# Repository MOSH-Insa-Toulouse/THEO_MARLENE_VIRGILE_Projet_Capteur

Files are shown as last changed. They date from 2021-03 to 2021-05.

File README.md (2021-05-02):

# THEO_MARLENE_VIRGILE_Projet_Capteur
Ce projet s'inscrit dans l'UF **"Du capteur au banc de Test"** en 4ème année Génie Physique, à l'INSA de Toulouse. 
***
Ce dernier a pour but l'élaboration d'un **capteur de déformation** à bas coût à base de graphite, dont le fonctionnement est basé sur le principe de déplacement des électrons entre les nanoparticules par effet tunnel. 
La contrainte mécanique appliquée modifiant la distance entre les particules, la conductivité électrique de la couche de graphite subit elle aussi une modification. La déformation du capteur créé grâce à un dépôt au crayon à papier engendre donc une variation de résistance alors mesurable.
*** 
Dans ce dossier sont présentées les différentes étapes que nous avons suivies : du design de notre shield, à notre code Arduino en passant par la réalisation d'une application pour téléphone et d'un banc de mesure réalisé en impression 3D. 

## Sommaire 

* [1. Description du projet et détail des livrables](#PremiereSection) 
* [2. Arduino](#DeuxiemeSection)
  * [2.1. Librairies utilisées](#DeuxiemeSection1)
  * [2.2. Code Arduino](#DeuxiemeSection2)
* [3. KICAD](#TroisiemeSection)  
  * [3.1 Symboles et empreintes](#TroisiemeSection1)
  * [3.2 Schématique](#TroisiemeSection2)
  * [3.3 Placement des composants](#TroisiemeSection3)
  * [3.4 Visualisation 3D](#TroisiemeSection4)
* [4. Fabrication du shield](#QuatriemeSection)
  * [4.1 Réalisation du PCB](#QuatriemeSection1)
  * [4.2 Perçage et soudure](#QuatriemeSection2)
* [5. Application Android](#CinquiemeSection) 
* [6. Tests](#SixiemeSection)
  * [6.1. Banc de test](#SixiemeSection1)
  * [6.2. Résultats obtenus](#SixiemeSection2)
  * [6.3. Analyse des résultats et discussion](#SixiemeSection3)
* [7. Datasheet](#SeptiemeSection)

## 1. Description du projet et détail des livrables

Liste des livrables :

- [x] Un code Arduino permettant une mesure de résistance et un contrôle des fonctionnalités Bluetooth, OLED... 
- [x] Un shield PCB
- [x] Une application android APK 
- [x] Un protocole du banc de test
- [x] Une datasheet des capteurs de déformation

Dans un premier temps, nous avons réalisé un **code Arduino** fonctionnel permettant de contrôler un amplificateur transimpédance, un encodeur rotatoire, un écran OLED ainsi qu'un module Bluetooth. Nous l'avons ensuite testé en effectuant nos premiers branchements.
Ensuite, nous avons réalisé le design de notre **shield** à l'aide du logiciel *KICAD*, nous l'avons fabriqué, puis nous avons assemblé nos composants dessus.   
A la suite de cela, nous avons utilisé le logiciel *MIT App Inventor* afin de développer une **application téléphone APK**, capable de communiquer et recevoir des données à distance à l'aide du module Bluetooth (notamment de récupérer la résistance ressentie par le capteur et de l'afficher sur un graphique).    
Nous avons également designé puis réalisé, un **banc de mesure** en impression 3D, qui, à l'aide d'un servomoteur nous permet de caractériser la réponse en déformation de nos futurs capteurs.   
Finalement, nous sommes passés à la phase de tests et avons créé nos capteurs, en les "coloriant" avec divers types de crayons à papier (HB,B,...). Nous avons ensuite caractérisé ces derniers en récupérant leur résistance en fonction de leur déformation, et avons ainsi pu établir une **datasheet**.

## 2. Arduino

### 2.1. Librairies utilisées

Pour développer notre code, nous avons utilisé plusieurs librairies :["Adafruit_GFX_Library"](/Librairies/Adafruit_GFX_Library) et ["Adafruit_SSD1306"](/Librairies/Adafruit_SSD1306) nous permettant le contrôle de nos modules, ainsi que la librairie [Adafruit_BusIO](/Librairies/Adafruit_BusIO) permettant de gérer la connexion en I2C et SPI.

### 2.2. Code Arduino

Le code [prog_arduino](/Programme%20Arduino/prog_arduino) développé sous Arduino IDE permet d'assurer la communication de tous les éléments de notre carte Arduino (Module Bluetooth, Oled et encodeur rotatoire) afin de réaliser des fonctions voulues. Nous avons ainsi réalisé quatre menus différents qui permettent de réaliser des tâches différentes. 

- Le premier menu permet d'afficher sur l'Oled la valeur de résistance de la jauge de contrainte traduite par l'acquisition de la tension de sortie de notre circuit électronique. Il permet aussi d'envoyer via le module bluetooth la valeur de tension mesurée entre 0 et 5 volts, sous la forme d'un nombre codé en 8 bits : 0 correspondant à 0V et 255 correspondant à 5V. L'objectif de cet envoi est d'ensuite le récupérer via notre application APK pour pouvoir traiter les données.
- Le second menu est assez similaire. La seule différence réside sur l'affichage de l'Oled. On n'affiche plus la valeur de résistance mais la valeur de tension. 
-  Le troisième menu permet de définir un temps d'acquisition sur l'application. On choisit la valeur en secondes grâce à l'encodeur rotatoire et lorsqu'on sélectionne la valeur choisie, elle s'envoie par Bluetooth pour être récupérée et enregistrée par l'application.
-  Le quatrième menu fonctionne de la même manière que le troisième mais permet de changer la valeur de R2 que l'on a laissé variable afin de s'adapter à la plage de mesure de la résistance du capteur. On entre la valeur voulue grâce à l'encodeur rotatoire. 

Les codes contenus dans les dossiers [BT_Test](/Programme%20Arduino/BT_Test), [ENC_TEST](/Programme%20Arduino/ENC_TEST) et [OLED_TEST](/Programme%20Arduino/OLED_TEST) permettent de vérifier individuellement l'état de fonctionnement de chaque module ajouté à notre shield. 

Enfin, Le code Arduino [Servomoteur](/Programme%20Arduino/Banc%20de%20test/Servomoteur) permet de contrôler notre banc de test et sera plus amplement expliqué dans la partie **6. Tests**.

## 3. KICAD

### 3.1. Symboles et empreintes
- Module Bluetooth 

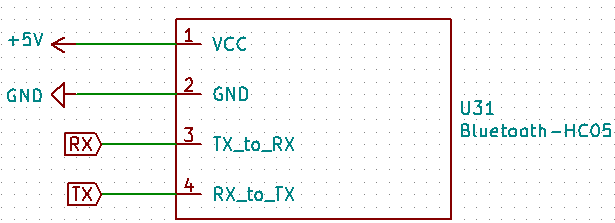
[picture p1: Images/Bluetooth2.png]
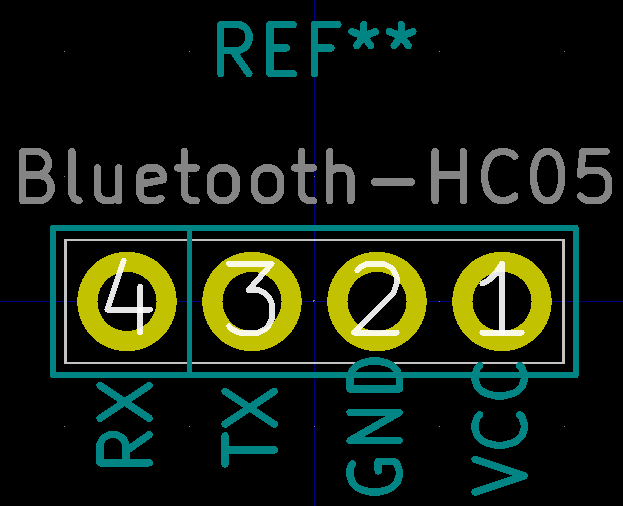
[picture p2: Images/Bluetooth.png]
 

- Encodeur rotatoire 

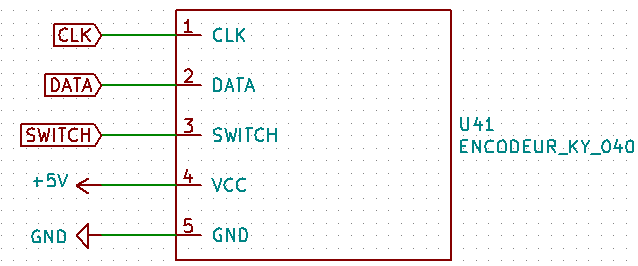
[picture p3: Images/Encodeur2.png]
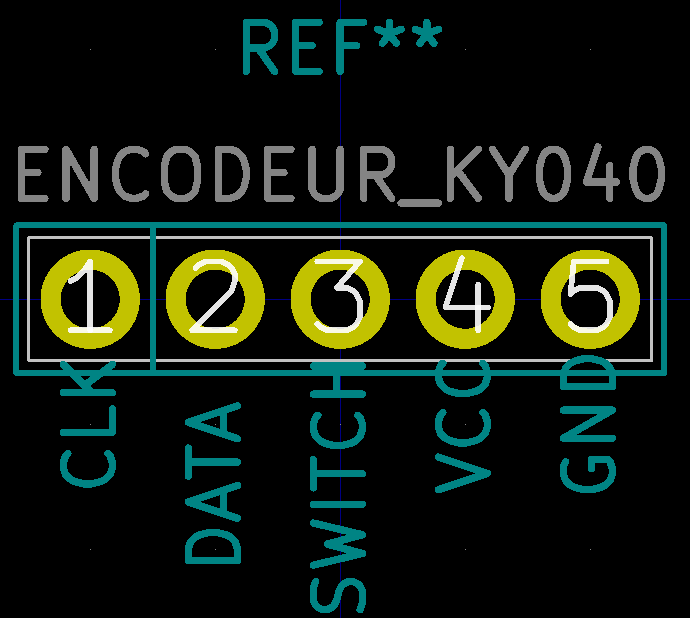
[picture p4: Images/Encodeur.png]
 

- Ecran OLED 

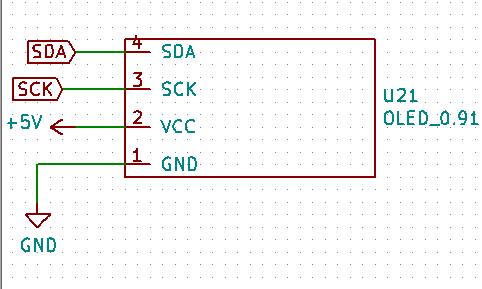
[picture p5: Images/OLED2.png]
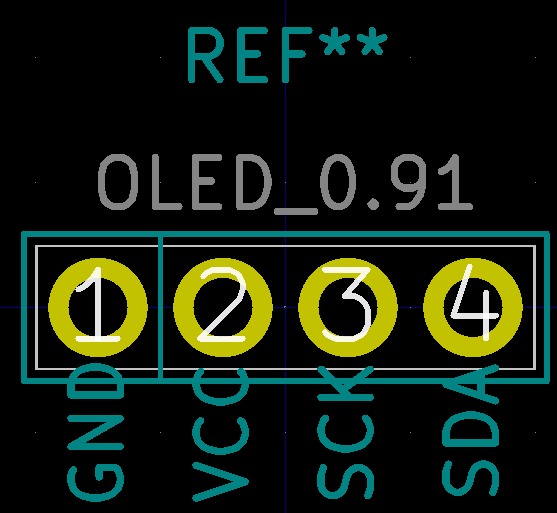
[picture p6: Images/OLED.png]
 

- Amplificateur LTC 1050

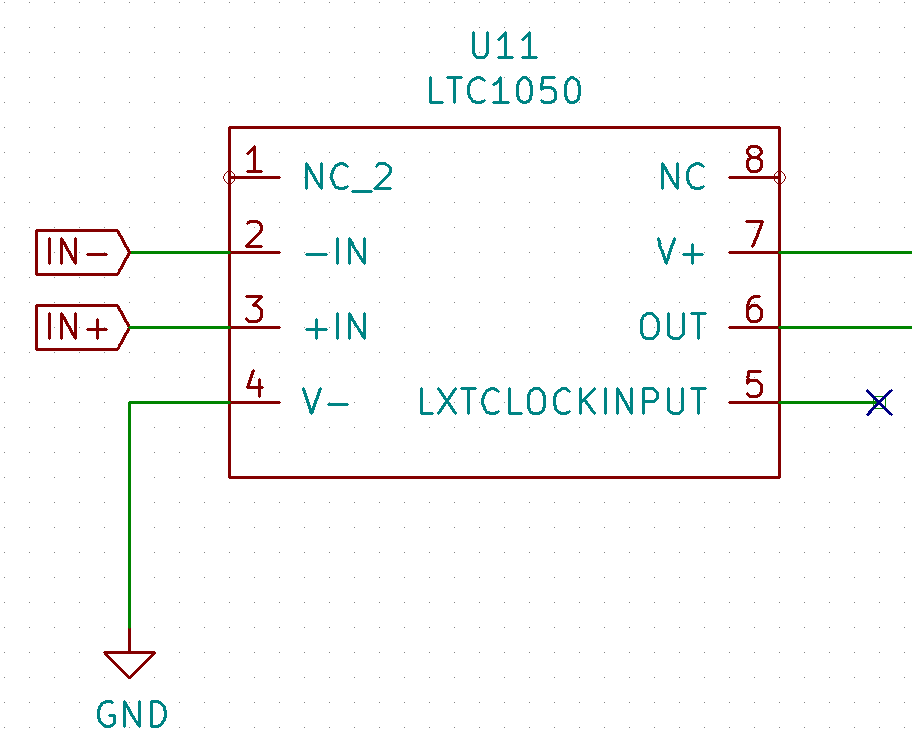
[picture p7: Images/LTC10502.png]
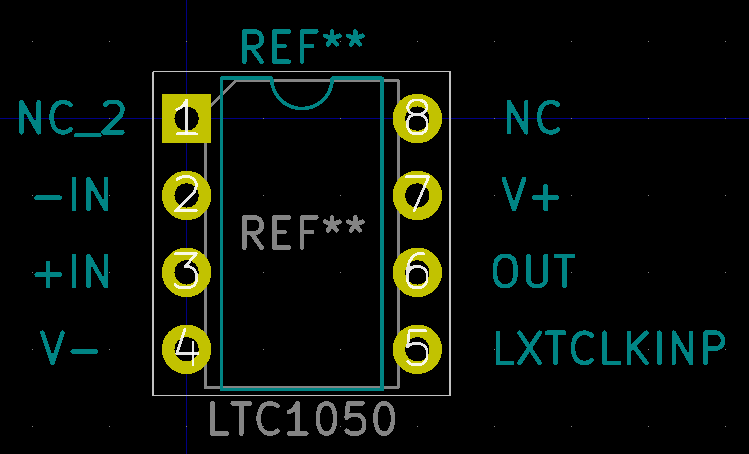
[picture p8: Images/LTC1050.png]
 

### 3.2. Schématique de l'ensemble 

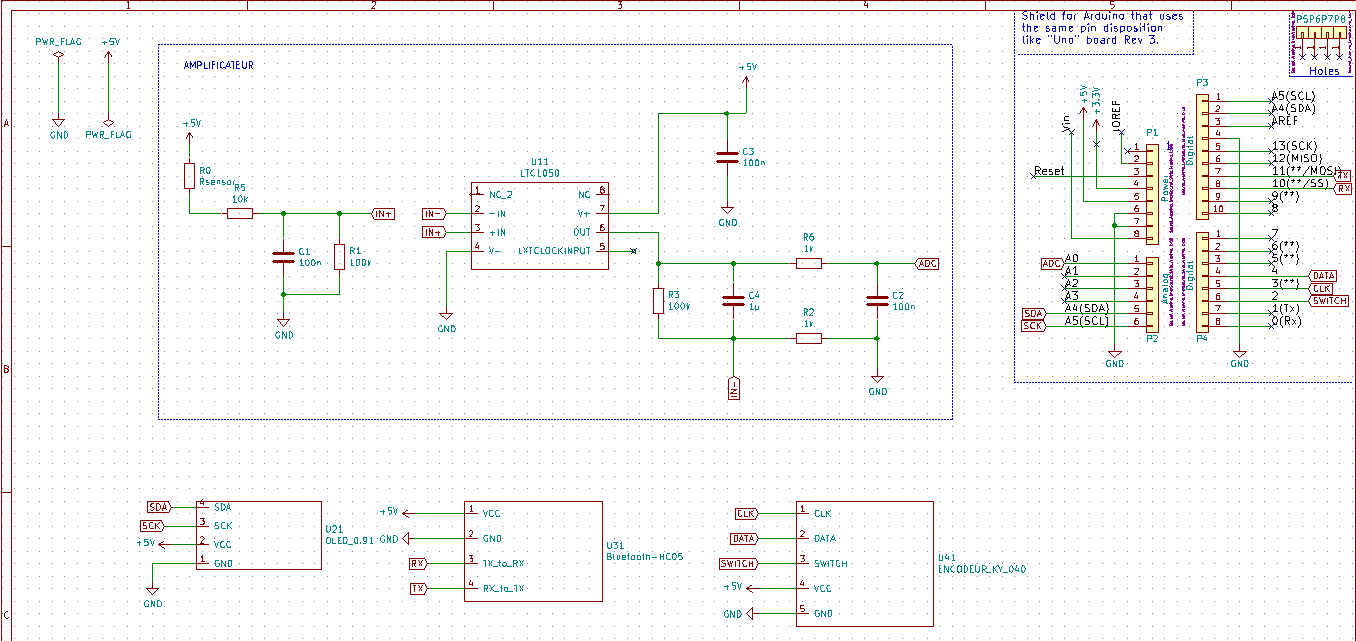
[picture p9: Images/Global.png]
Glob


Une fois les empreintes créées, nous avons pu réaliser le Eeschema de notre shield. En haut à droite sont représentées les broches de la carte Arduino. Au centre est représenté l'amplificateur transimpédance, et en bas l'écran OLED, le module Bluetooth et l'encodeur rotatoire.

### 3.3. Placement des composants
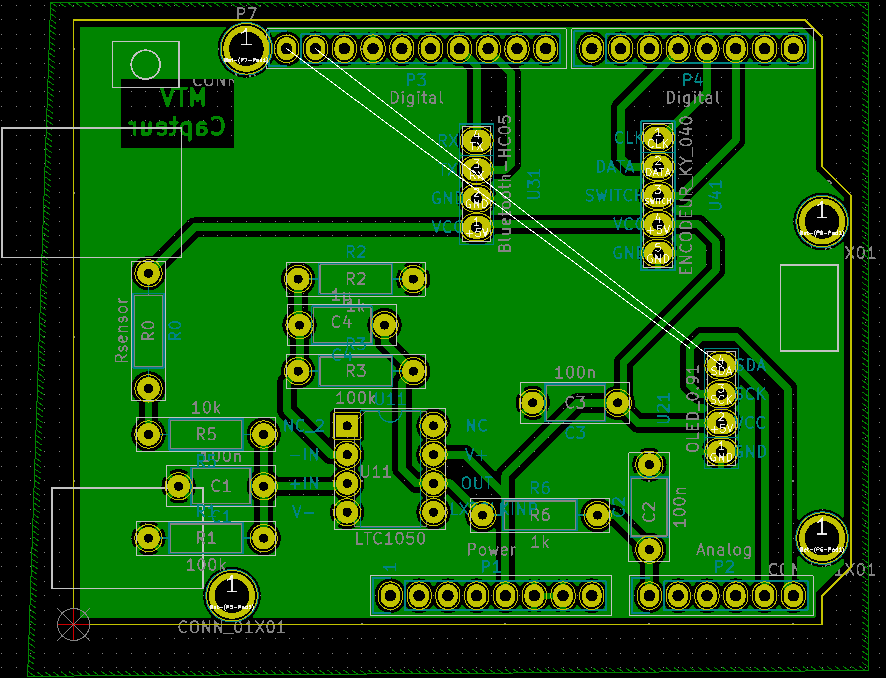
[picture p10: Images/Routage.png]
Rout


### 3.4. Visualisation 3D
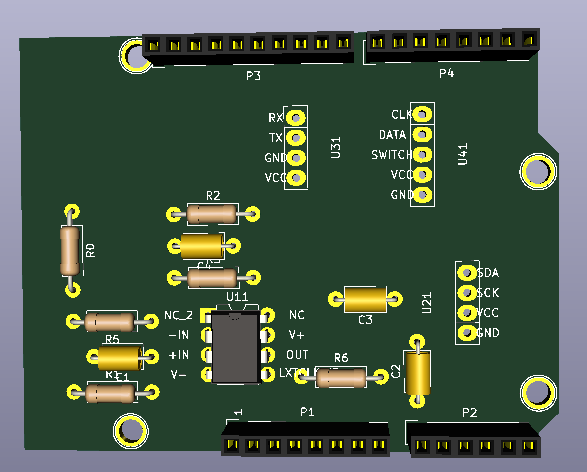
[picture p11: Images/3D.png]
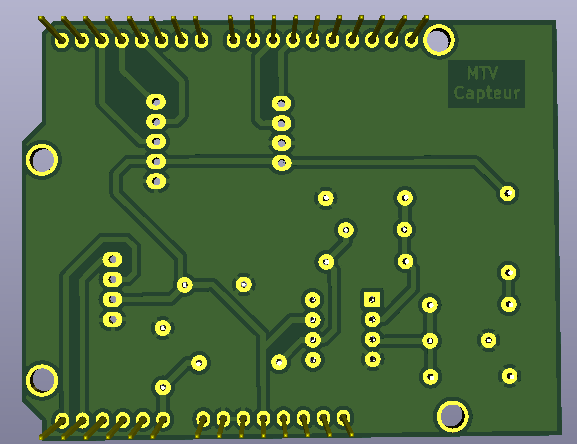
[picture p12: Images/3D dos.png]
 

## 4. Fabrication du shield
### 4.1. Réalisation du PCB

 Nous avons ensuite pu fabriquer le PCB sur une plaquette d'epoxy recouverte d'une fine couche de cuivre (environ 60µm).  
 Tout d'abord, nous avons imprimé notre modélisation du PCB sur du papier calque, puis, une insolation aux UV pendant 2 minutes a permis de transposer cette "silhouette" sur notre couche d'epoxy, permettant ainsi de déposer une résine protectrice, qui grâce à un révélateur, a pu être retirée aux endroits désirés.  
 Ensuite, la plaquette a été déposée dans un bain de perchlorure de fer afin d'être gravée (environ 8 minutes). A la suite de cela, le cuivre non protégé par la résine a alors été retiré, permettant d'obtenir le PCB modélisé en amont.  
 Pour finir, de l'acétone a été appliquée sur la plaquette pour éliminer les dernières traces de résine.

### 4.2. Perçage et soudure

Une fois le PCB réalisé, nous sommes passés au perçage de trous sur notre plaquette à l'aide d'une perçeuse électrique afin d'insérer nos composants : 
- 0.8mm de diamètre pour l'AOP, les résistances et les capacités
- 1mm de diamètre pour les connecteurs de l'Arduino et des headers des différents modules (pinces du capteur, bluetooth, encodeur rotatoire, écran OLED)

Enfin, nous avons soudé chaque composant à l'aide d'un fer à souder.

## 5. Application Android

[L'application](/Application) développée sous MIT App Inventor, un site internet permettant de designer des applications en ligne, permet d'établir la liaison entre les données relevées par l'arduino et le traitement de celles-ci, en direct puis via la création d'un fichier de données. 

Concrètement, l'application a été designée pour corréler avec le code arduino (cf 2.). Elle permet ainsi de se connecter à un module bluetooth chargé d'envoyer la tension relevée, qui sera traduite en résistance pour le capteur. Lorsque l'on est connecté, l'application est capable d'effectuer 3 tâches principales : 
- Relever la tension envoyée par Bluetooth, afficher la valeur de résistance correspondante, de manière numérique et graphique et la traduire dans un fichier texte. Cette fonction est commandée par un système Start/Stop.
- Effectuer une acquisition selon un temps donné. Il faut au préalable définir le temps d'acquisition via l'arduino. Ce temps vient remplacer le Start/Stop, sinon la fonction est la même que précédemment.
- Modifier la valeur de résistance de R2. Pour cela, il faut rentrer la valeur via l'arduino.

## 6. Tests
### 6.1. Banc de test

Pour réaliser nos tests, nous avons utilisé 2 bancs différents ; l'un déjà existant et pensé par nos prédécesseurs et un autre par nos soins lors de la réalisation du projet.

#### Le [banc de test](/Banc%20de%20test) que nous avons imaginé a été modélisé via un logiciel de CAO et ensuite imprimé grâce à une imprimante 3D. 

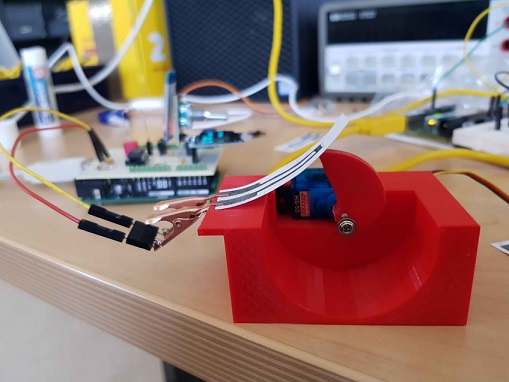
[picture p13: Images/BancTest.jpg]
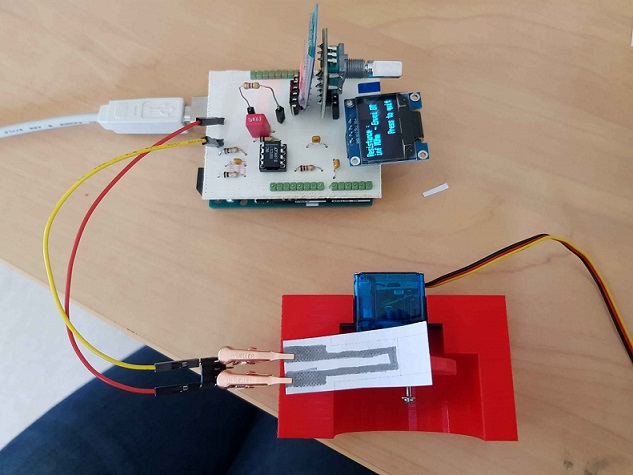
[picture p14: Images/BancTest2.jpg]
   

Il permet de mesurer la déformation du capteur en fonction du temps grâce à une rotation induite par un servomoteur et répond à deux problématiques :
 - La première étant la limite principale du banc de test déjà existant : il était destructif. En effet à chaque utilisation de celui-ci le capteur devenait inutilisable par la suite. Il nous était donc impossible de revenir aux valeurs initiales de résistances après passage du capteur sur le banc de test. 
- La seconde étant la volonté d’observer l’évolution en dynamique de la réponse du capteur afin de déterminer une potentielle fatigue de celui-ci lors d’un test cyclique. 

Nous avons donc réfléchi à un design permettant une installation fixe du capteur qui ne nécessitait plus d’action extérieure au cours de la mesure, et qui pouvait faire périodiquement une application de contrainte identique sur notre capteur. Pour cela, notre banc a été conçu en 3 parties : le socle, la pièce « escargot » et le servomoteur, pilotés via [un code Arduino](/Programme%20Arduino/Banc%20de%20Test/Servomoteur) supplémentaire. 

**Le socle**

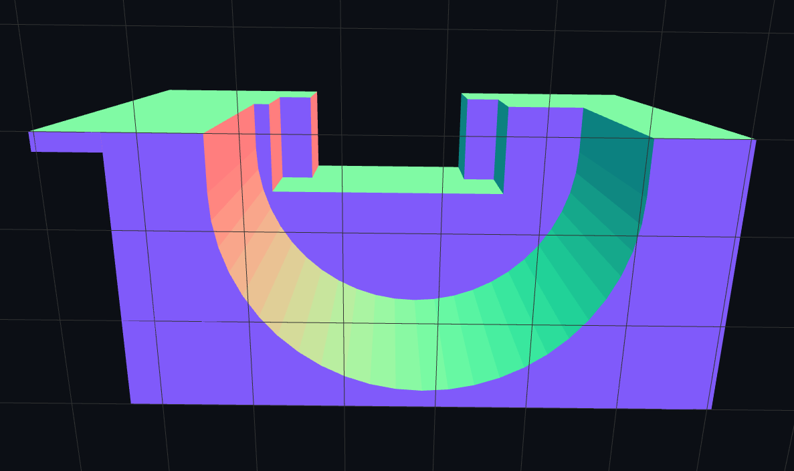
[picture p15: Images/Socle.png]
 
Le socle est la pièce massive qui permet de fixer le servomoteur et le capteur afin de ne pas avoir à retoucher le système entre les mesures.  

•	 La languette sur le côté gauche représente la zone permettant de fixer le capteur à l’aide des pinces conductrices.   
•	 Le demi cercle vide au milieu de la pièce correspond à la zone permettant la rotation de la pièce « escargot ».  
•	 L’encoche qui traverse la pièce dans la largeur permet de glisser le servomoteur et de le maintenir dans la position souhaitée.  

**La pièce « escargot »**

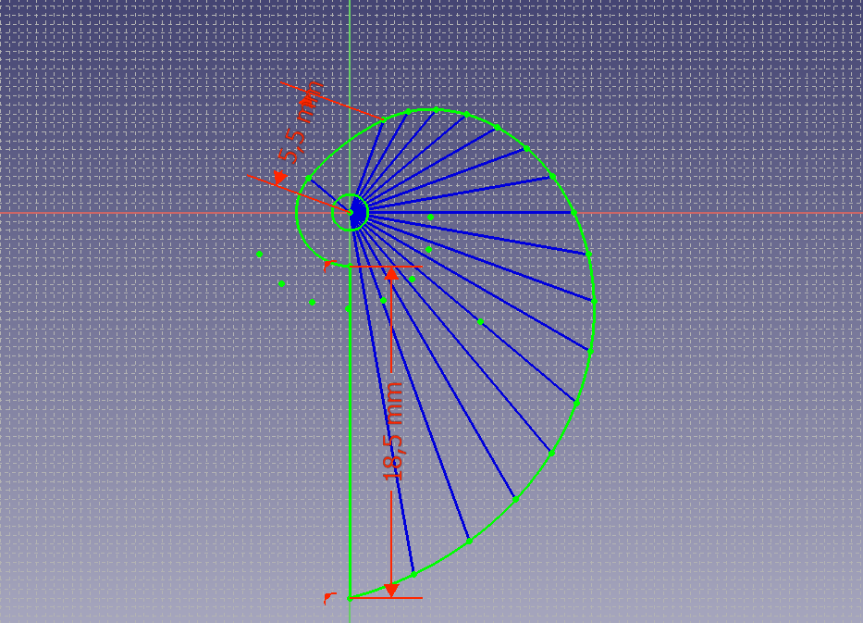
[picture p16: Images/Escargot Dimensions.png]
 

Cette pièce est un embout pour le servomoteur : l’extrémité libre du capteur repose dessus lorsqu’il est fixé sur le banc. 
Le rayon de l’embout augmente d’un millimètre tous les dix degrés de rotation ce qui permet d’avoir une variation du rayon entre 5,5 mm et 21,5 mm sur l’ensemble de la rotation du servomoteur.   

Nous souhaitions pouvoir remonter à la déformation en connaissant la longueur du rayon or après plusieurs tentatives, nous nous sommes rendus compte qu’il était difficile de remonter à cette valeur en compression avec la composition géométrique de ce banc de test.   

**Le servomoteur**

Nous avons choisi d’utiliser le servomoteur SG90 car parmi ceux à notre disposition, c’est celui dont les dimensions étaient les plus adaptées pour notre capteur.   
En effet sa petite taille nous permet d’y fixer un embout de plus petite taille qui nous assure de rester dans le domaine de la déformation élastique du papier puisque nous pouvons  appliquer des déformations plus faibles et plus précises.   
Utiliser un servomoteur nous permet de gérer facilement la rotation de la pièce «escargot», et in extenso de fixer facilement la plage de déformation du capteur à l’aide du code Arduino. 

**Le code Arduino**

Nous avons utilisé [ce code Arduino](/Programme%20Arduino/Banc%20de%20test/Servomoteur) qui nous permet de changer la plage de rotation du servomoteur. Il nous permet en modifiant les lignes 17 et 22 de changer la plage de rotation du servomoteur. L’objectif étant de balayer la plus grande différence de rayon possible tout en ne dépassant jamais le bout de course de la pièce escargot afin de ne pas détruire le capteur.  

#### Le banc de test déjà réalisé composé de 7 demi-cercles dont les rayons varient de 1 à 2,5 cm. 
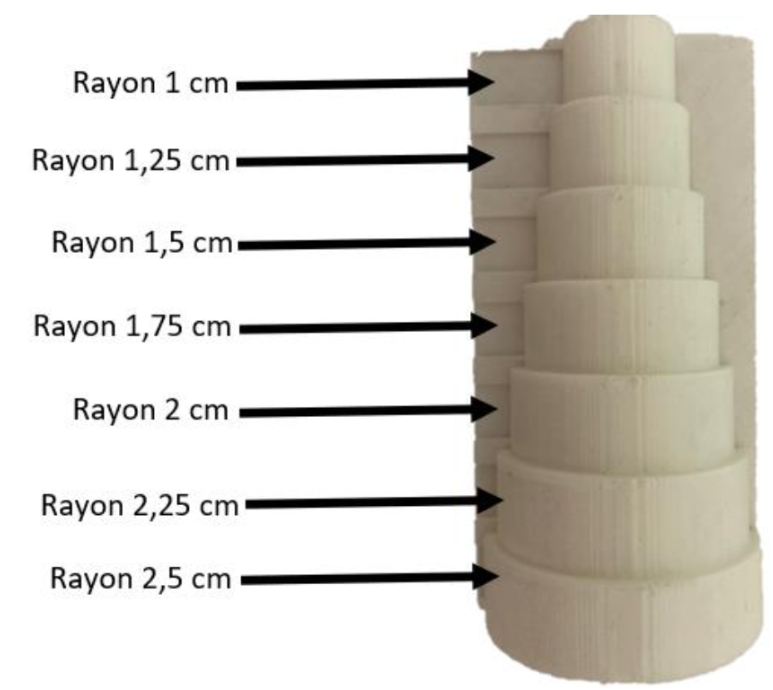
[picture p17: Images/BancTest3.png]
 

### 6.2. Résultats obtenus

**Avec le banc de test utilisant le servomoteur**

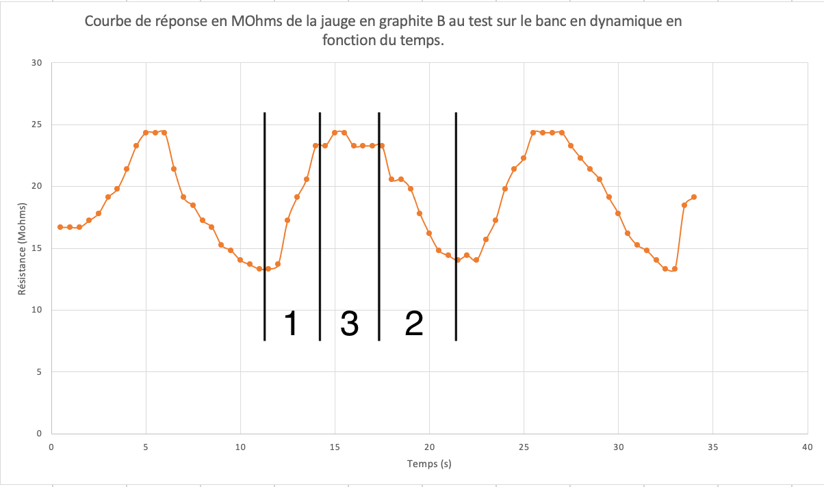
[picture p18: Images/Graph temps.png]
   

Nous pouvons voir que la jauge réagit de façon périodique à la contrainte du banc en dynamique. 
En effet, lors de la diminution du rayon de la pièce en escargot, nous observons une augmentation quasi-linéaire de la résistance (cf courbe ci-dessus zone 1). 
Lors de l'augmentation de celui-ci, nous observons une diminution quasi-linéaire de la résistance de la jauge de contrainte (cf courbe ci-dessus zone 2).
Nous observons également une plage de données instable entre ces deux phases. Cette réponse du capteur est due à l’imperfection de notre banc (cf courbe ci-dessus zone 3). En effet, lorsque l’on arrive au bout de la course du servomoteur, le capteur ne suit pas complètement l’évolution du rayon de courbure, et entre en contact avec une autre surface de la pièce en « escargot » que celle souhaitée. 

**Avec le banc de test déjà réalisé**

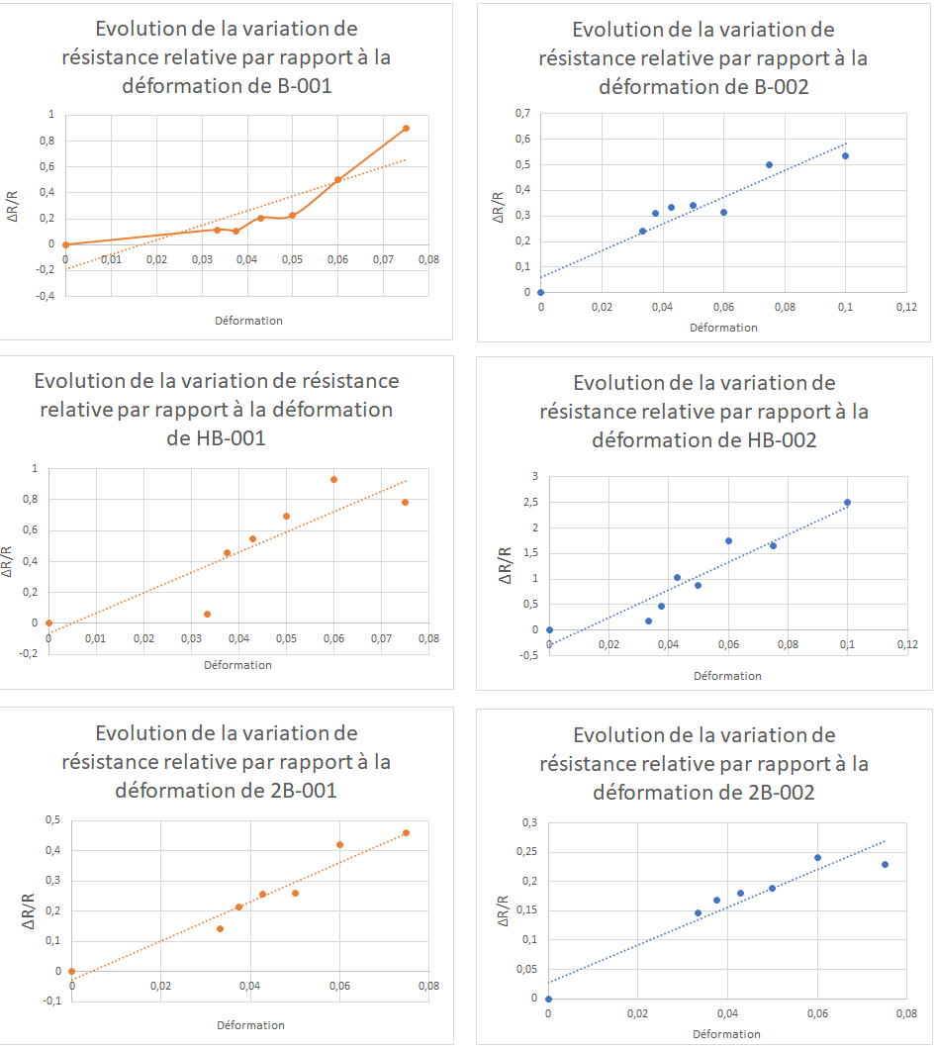
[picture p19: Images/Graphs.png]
 

Comme nous pouvons l’observer sur les graphiques ci-dessus, la plupart des réponses des jauges aux déformations appliquées à l’aide du banc de test statique suivent une évolution quasi-linéaire. 

La résistance sans contrainte varie du simple au double entre deux jauges produites par le même type de crayon à papier. 

Les variations de résistance sont plus importantes lorsque la dureté du crayon est plus élevée. En effet, pour le HB nous avons pu observer au maximum une variation de 5 à 20 MOhms et pour le 2B de 4 à 5 MOhms. 

Les facteurs de jauge obtenus en faisant une approximation linéaire sont de :
- 6,5 et 3,2 pour les essais 1 et 2 avec des jauges dessinées avec des crayons 2B
- 6,1 et 11,4 pour les essais 1 et 2 avec des jauges dessinées avec des crayons B
- 13,1 et 27,2 pour les essais 1 et 2 avec des jauges dessinées avec des crayons HB

### 6.3. Analyse des résultats et discussion

Nous observons à l’aide de **notre banc de test** utilisant le servomoteur que le capteur retrouve sa valeur initiale de résistance entre chaque mise sous contrainte. Nous n’observons donc pas de fatigue de la jauge dans la gamme de contraintes que nous appliquons : il faudrait effectuer des tests sur de très longues périodes avant d’apercevoir d’éventuelles fatigues. 

Concernant les imprécisions de la zone de mesure se situant en bout de course du servomoteur, plusieurs améliorations sont envisageables : 
 - Concevoir la pièce « escargot » en miroir, de façon à toujours avoir un rayon plus petit sous la jauge au lieu du contraire actuellement
 - Repenser la pièce afin de pouvoir fixer directement l’extrémité du capteur à la pièce « escargot »

Nous aurions pu également réfléchir en amont au calcul de contrainte qui aurait été plus pertinent qu’un simple relevé de résistance.  
  
Ces différents résultats mettent en valeur les avantages et les limites de ce type de jauges de contrainte.   

Pour ce qui est du **banc de test déjà réalisé**, nous constatons que les jauges réalisées ont, d'après les essais, des facteurs de jauge très élevés avec l’utilisation de crayons à papier à pointe dure, mais que, si le crayon dépose trop peu de graphite, des problèmes de continuité électrique se posent.  

Une des principales limites est donc la dépose du graphite. En effet, nous remarquons des différences de quasiment un facteur 2 entre les facteurs de jauge des capteurs dessinés en 2B, B et HB. 
Ces différences peuvent être dûes à :
 - la non-répétabilité de la mesure et la destruction du capteur en fonction de la manipulation de la jauge et du banc
 - le dépôt de graphite sur le papier : la pression avec le crayon à papier, le nombre de passages du crayon, la précision du tracé    

Il faudrait réfléchir à un procédé permettant un dépôt uniforme, précis et répétable. Une impression mécanique automatisée serait une option pour rendre les facteurs de jauge plus constants.  

Nous pouvons tout de même conclure que la confection de jauges de contrainte en graphite est réalisable et permet de créer des jauges avec de très bon facteurs de jauge. 
Néanmoins, le processus de dessin doit être optimisé car il y a beaucoup trop de paramètres qui ne permettent pas de garantir la qualité de la jauge de contrainte. 

## 7. Datasheet

La [Datasheet](/Datasheet) présente l'ensemble des caractéristiques des jauges que nous avons réalisées ainsi que du shield qui permet de traduire un relevé de tension en mesure de résistance. L'objectif final est de revenir à une mesure de déformation.

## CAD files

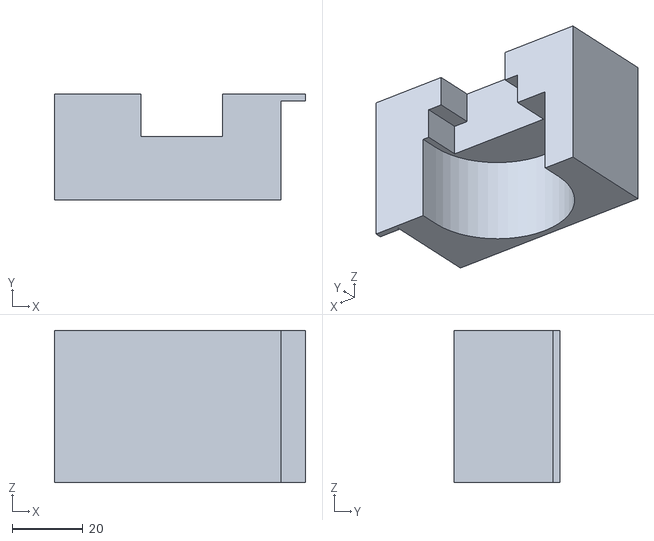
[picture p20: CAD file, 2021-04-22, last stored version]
Banc de test/socle final.stl
71.0 x 30.0 x 43.0

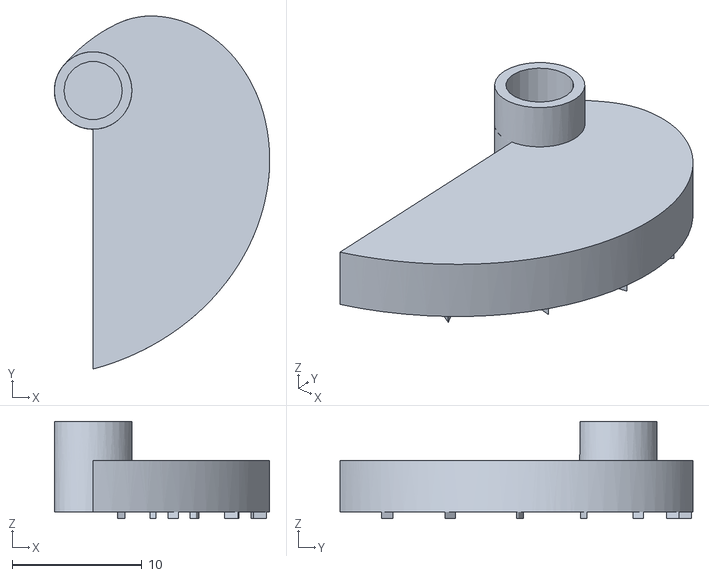
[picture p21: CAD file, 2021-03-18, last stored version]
Banc de test/pièce servomoteur.stl
16.6 x 27.3 x 7.50

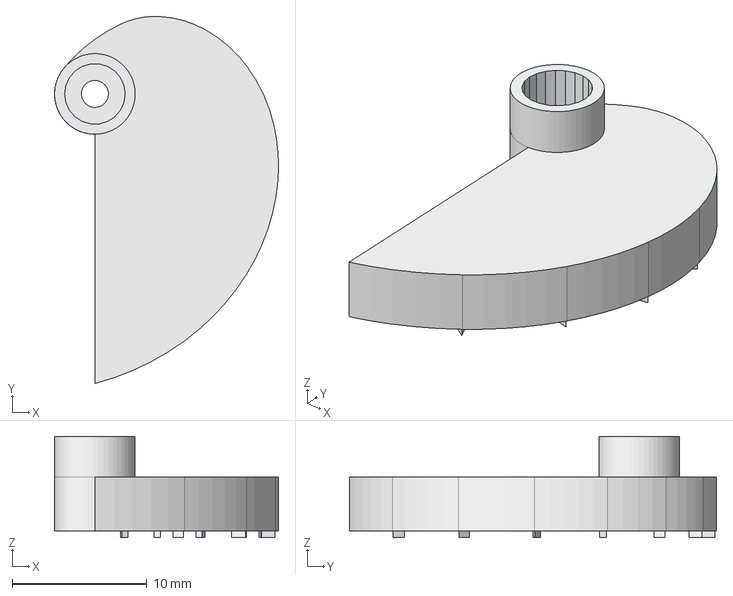
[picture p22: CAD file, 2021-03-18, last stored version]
THEO_MARLENE_VIRGILE_Projet_Capteur-main/Banc de test/Piece_Servomoteur.FCStd
16.6 x 27.2 x 7.50 mm

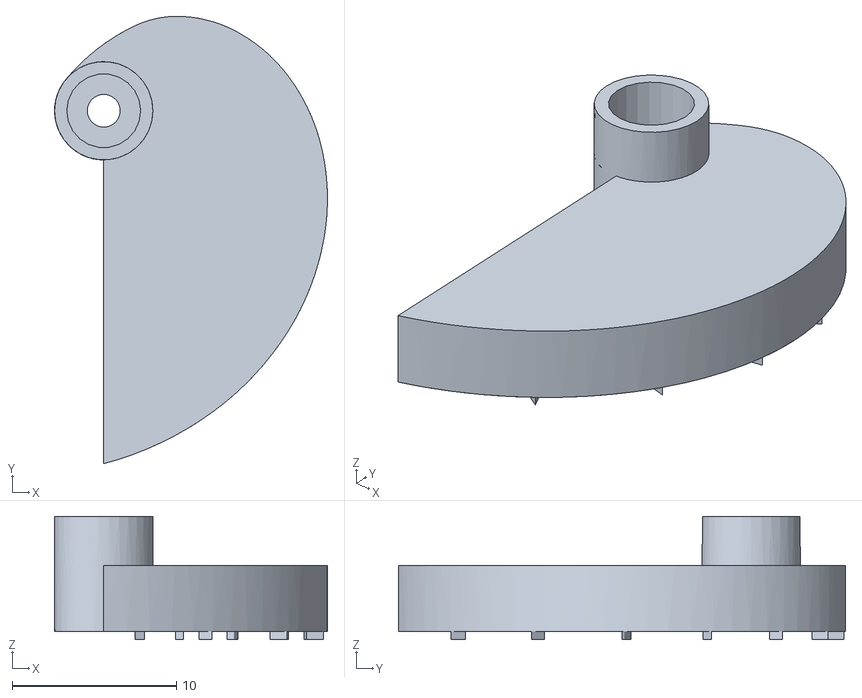
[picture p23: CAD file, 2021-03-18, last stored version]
Banc de test/Pièce servomoteur v2.stl
16.6 x 27.3 x 7.50

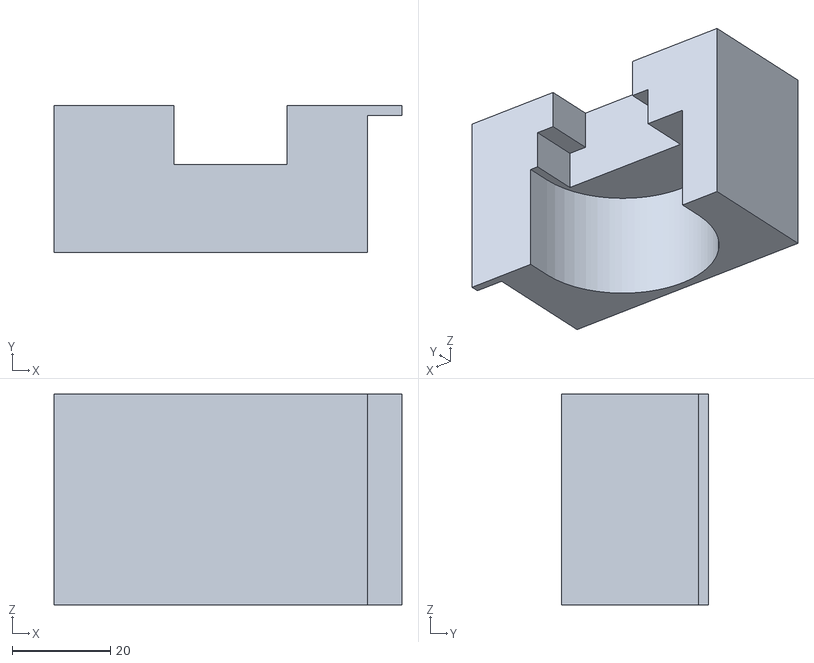
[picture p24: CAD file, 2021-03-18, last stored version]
Banc de test/socle banc test.stl
71.0 x 30.0 x 43.0

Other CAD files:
THEO_MARLENE_VIRGILE_Projet_Capteur-main/Banc de test/socle banc de test.FCStd
Banc de test/socle banc de test.FCStd

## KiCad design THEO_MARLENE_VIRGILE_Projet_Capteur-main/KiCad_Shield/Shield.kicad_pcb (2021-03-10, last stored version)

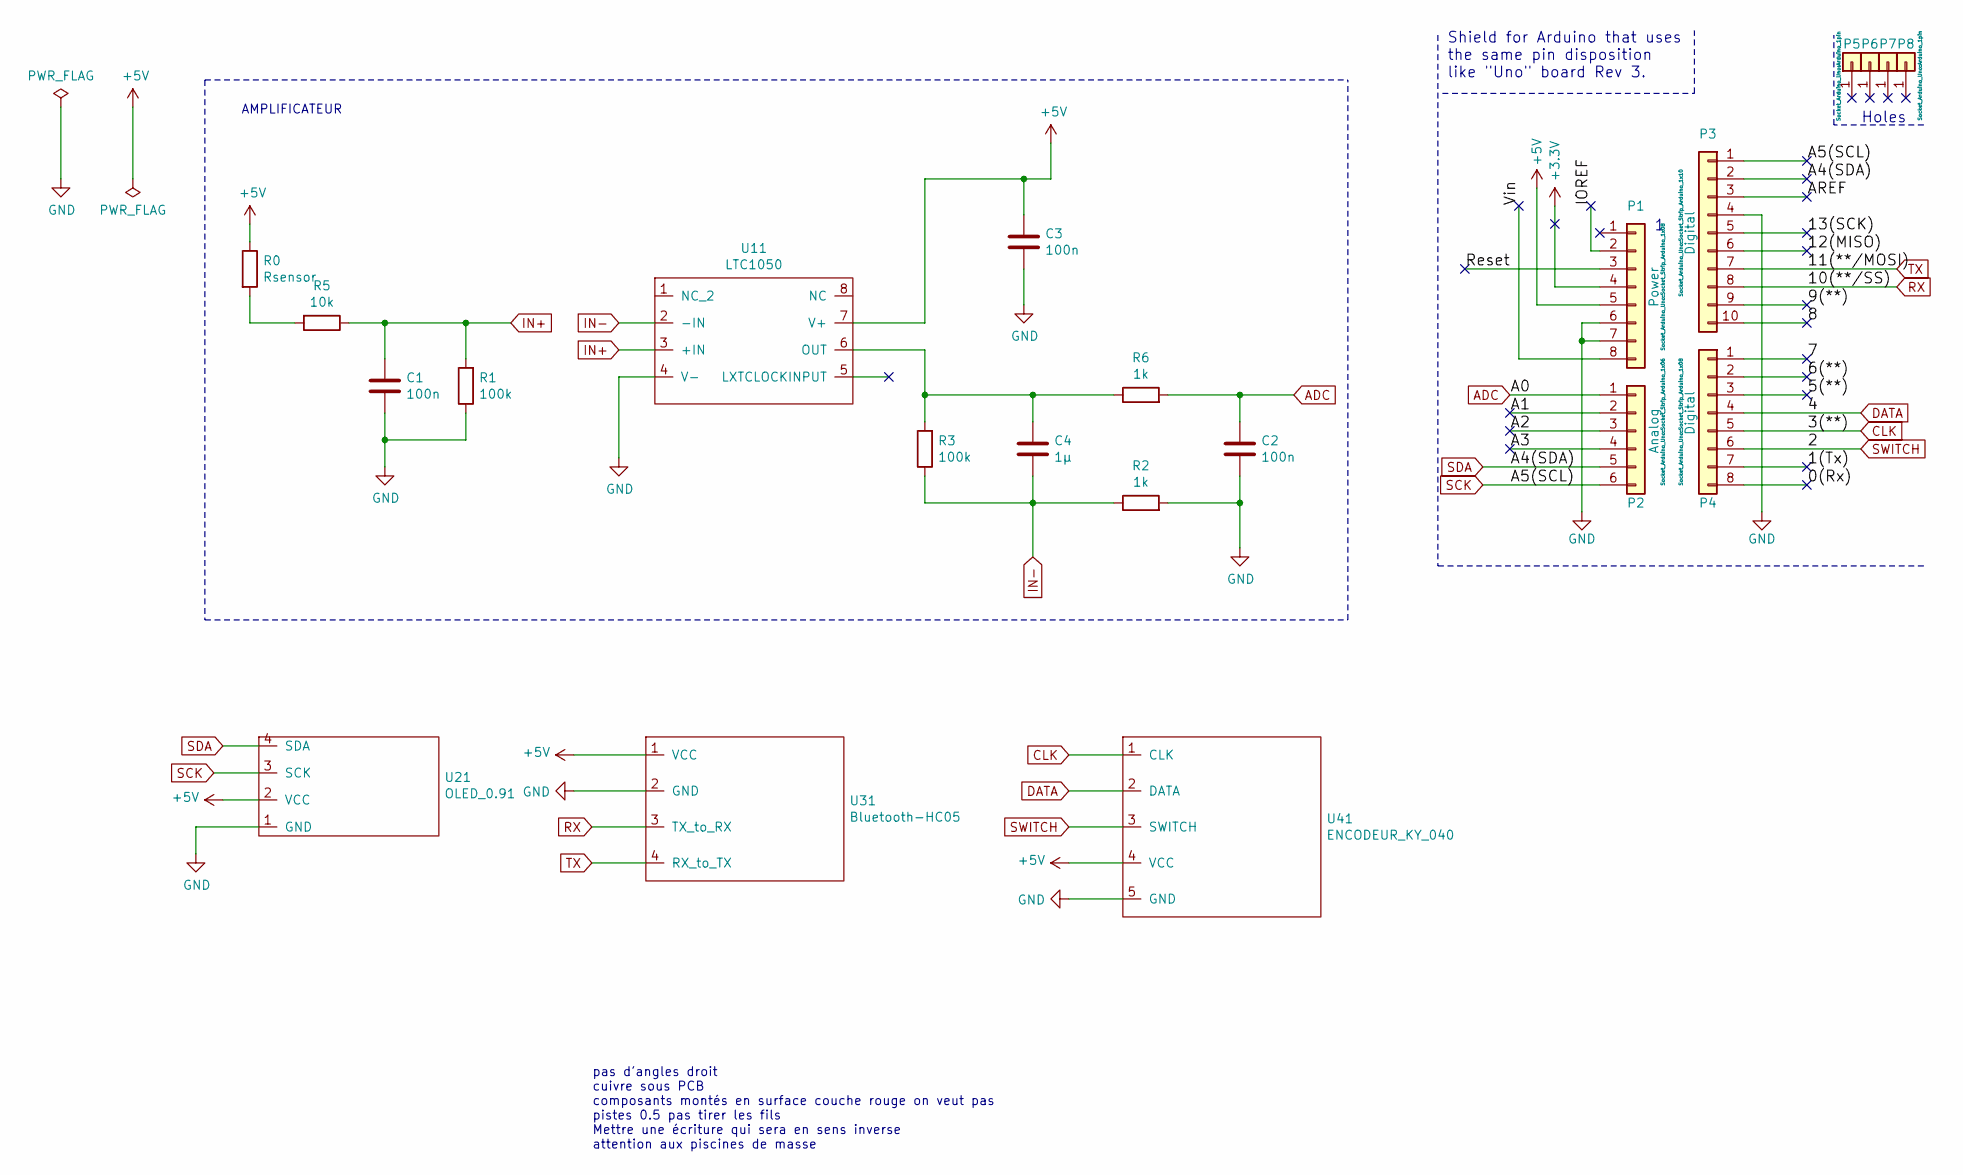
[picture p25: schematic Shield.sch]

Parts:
C1, C2, C3: 100n; C_Axial_L5.1mm_D3.1mm_P7.50mm_Horizontal
C4: 1µ; C_Axial_L5.1mm_D3.1mm_P7.50mm_Horizontal
P1: Power; Socket_Strip_Arduino_1x08
P2: Analog; Socket_Strip_Arduino_1x06
P3: Digital; Socket_Strip_Arduino_1x10
P4: Digital; Socket_Strip_Arduino_1x08
P5, P6, P7, P8: CONN_01X01; Arduino_1pin
R0: Rsensor; R_Axial_DIN0207_L6.3mm_D2.5mm_P10.16mm_Horizontal
R1, R3: 100k; R_Axial_DIN0207_L6.3mm_D2.5mm_P10.16mm_Horizontal
R2, R6: 1k; R_Axial_DIN0207_L6.3mm_D2.5mm_P10.16mm_Horizontal
R5: 10k; R_Axial_DIN0207_L6.3mm_D2.5mm_P10.16mm_Horizontal
U11: LTC1050
U21: OLED_0.91
U31: Bluetooth-HC05
U41: ENCODEUR_KY_040; ENCODEUR_KY040

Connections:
+3V3: P1.4
+5V: C3.1, P1.5, R0.1, U11.7 (V+), U21.2 (VCC), U31.1 (VCC), U41.4 (VCC)
/0(Rx): P4.8
/1(Tx): P4.7
/5(**): P4.3
/6(**): P4.2
/7: P4.1
/8: P3.10
/9(**): P3.9
/12(MISO): P3.6
/13(SCK): P3.5
/A1: P2.2
/A2: P2.3
/A3: P2.4
/AREF: P3.3
/IOREF: P1.2
/Reset: P1.3
/Vin: P1.8
ADC: C2.1, P2.1, R6.2
CLK: P4.5, U41.1 (CLK)
DATA: P4.4, U41.2 (DATA)
GND: C1.2, C2.2, C3.2, P1.6, P1.7, P3.4, R1.1, R2.2, U11.4 (V-), U21.1 (GND), U31.2 (GND), U41.5 (GND)
IN+: C1.1, R1.2, R5.1, U11.3 (+IN)
IN-: C4.2, R2.1, R3.1, U11.2 (-IN)
unnamed: C4.1, R3.2, R6.1, U11.6 (OUT)
unnamed: R0.2, R5.2
RX: P3.8, U31.3 (TX_to_RX)
SCK: P2.6, P3.1, U21.3 (SCK)
SDA: P2.5, P3.2, U21.4 (SDA)
SWITCH: P4.6, U41.3 (SWITCH)
TX: P3.7, U31.4 (RX_to_TX)

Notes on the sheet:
Holes
Shield for Arduino that uses the same pin disposition like "Uno" board Rev 3.
AMPLIFICATEUR
pas d'angles droit cuivre sous PCB composants montés en surface couche rouge on veut pas pistes 0.5 pas tirer les fils Mettre une écriture qui sera en sens inverse attention aux piscines de masse

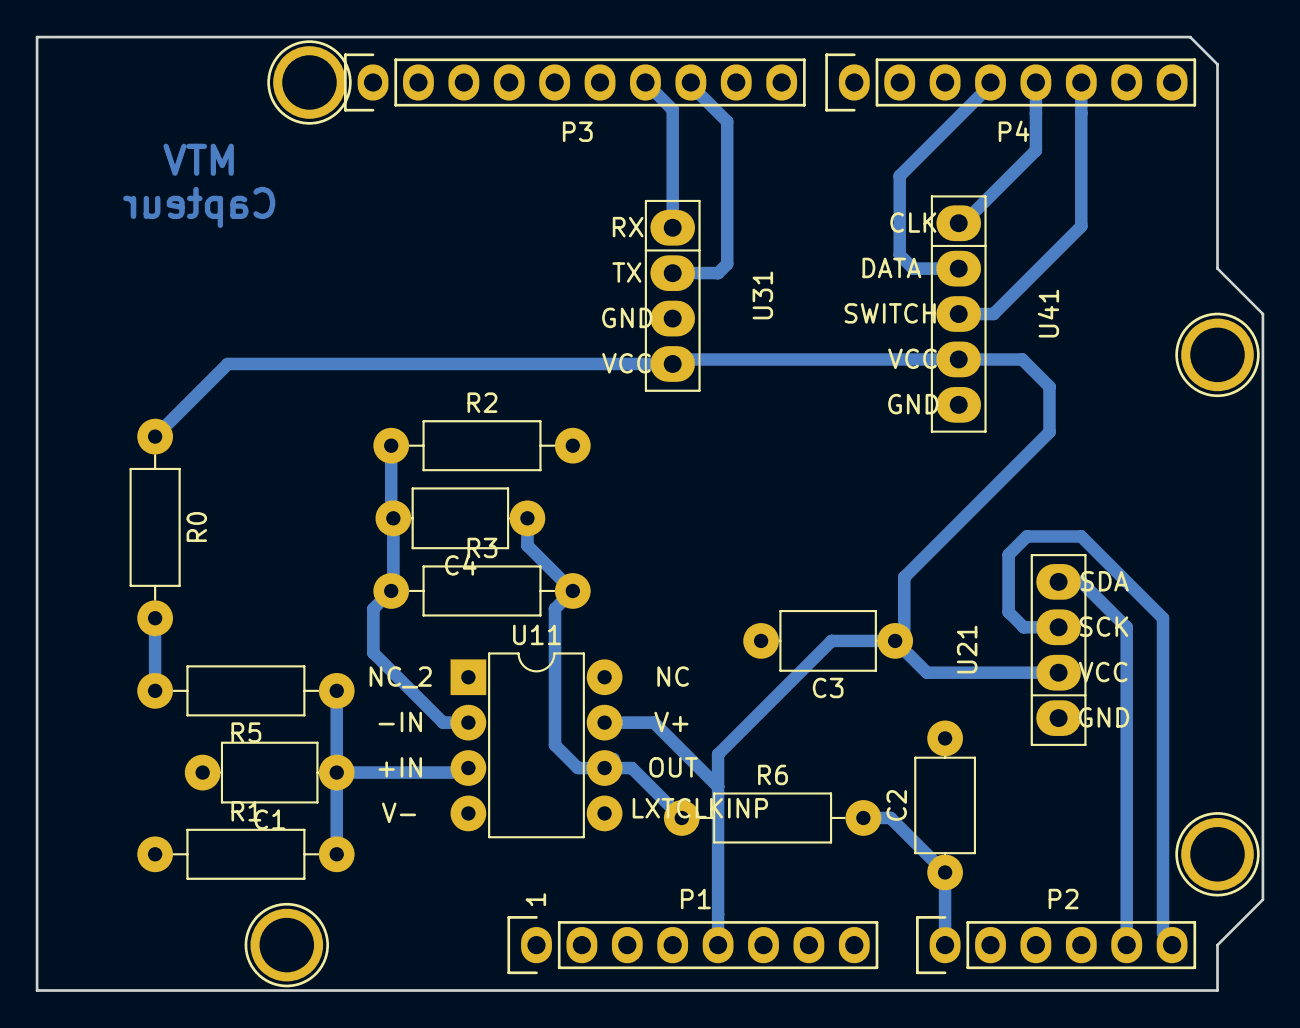
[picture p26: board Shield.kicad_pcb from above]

Board: 2 copper layers, 68.6 x 53.3 mm, 22 parts (0 on the bottom side), 14 nets.

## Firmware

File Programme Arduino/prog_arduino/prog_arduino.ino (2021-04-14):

  // Rotary Encoder

#define encoder0PinA  3  //CLK Output A Do not use other pin for clock as we are using interrupt
#define encoder0PinB  4  //DT Output B
#define Switch 2 // Switch connection if available
volatile unsigned int encoder0Menu_temp = 0;
volatile unsigned int encoder0Menu = 0;
volatile unsigned int Menu_State = 0 ;

volatile unsigned int action_encoder = 0; // retient quelle action effectuer pour l'encodeur
volatile unsigned int temps_acquisition_temp = 0;
volatile unsigned int temps_acquisition = 0;

volatile unsigned int val_R2_temp = 0;
volatile unsigned int val_R2 = 0;

int val_choisie = 0;
int temps_choisi = 0;

int State;
int Old_State;

  // Oled 

  // if any problem occurs make Ctrl+Maj+i and add Adafruit_BusIO_Register , Adafruit_SSD1306 , Adafruit_GFX

#include <Wire.h>
#include <Adafruit_GFX.h>
#include <Adafruit_SSD1306.h>
#include <Adafruit_BusIO_Register.h>
#include <Adafruit_I2CDevice.h>
#include <Adafruit_I2CRegister.h>
#include <Adafruit_SPIDevice.h>


#define SCREEN_WIDTH 128 // OLED display width, in pixels
#define SCREEN_HEIGHT 32 // OLED display height, in pixels

// Declaration for an SSD1306 display connected to I2C (SDA, SCL pins)
#define OLED_RESET 4 // Reset pin # (or -1 if sharing Arduino reset pin)
#define SCREEN_ADDRESS 0x3C ///< See datasheet for Address; 0x3D for 128x64, 0x3C for 128x32
Adafruit_SSD1306 display(SCREEN_WIDTH, SCREEN_HEIGHT, &Wire, OLED_RESET);

  // Bluetooth

#include <SoftwareSerial.h>
#define rxPin 10 //Broche 10 en tant que RX, � raccorder sur TX du HC-05
#define txPin 11 //Broche 11 en tant que RX, � raccorder sur TX du HC-05
#define baudrate 9600 
SoftwareSerial Serial_Phone(rxPin ,txPin); //D�finition du software serial

  // Transimp

#define ADCpin  0

  // Global variables 

float resistance = 0;
float tension;
int R1 = 100;
int R2 = 22;
int R3 = 100;
int R5 = 10;
int voltage_ADC;


  // Fonctions Encodeur

// doEncoder increments or decrements the variable encoder0Menu that is used to navigate into menues, between 4 of them, also used to increments the "temps_acquisition" variable
void doEncoder() {

  State = digitalRead(encoder0PinA);

  if (action_encoder == 0) {
  
    if (State != Old_State)
    {
      if (digitalRead(encoder0PinB) != State)
      {
        encoder0Menu_temp = (encoder0Menu_temp + 1) % 8;
        encoder0Menu = encoder0Menu_temp/2;
      }
      else {
        encoder0Menu_temp = (encoder0Menu_temp - 1) % 8;
        encoder0Menu = encoder0Menu_temp/2;
      }
    }

  }

  else if ((action_encoder == 1) and (temps_choisi == 0) and (Menu_State == 2)) {

    if (State != Old_State)
    {
      if (digitalRead(encoder0PinB) != State)
      {
        temps_acquisition_temp = (temps_acquisition_temp + 1) % 60;
        temps_acquisition = temps_acquisition_temp / 2;
      }
      else {
        temps_acquisition_temp = (temps_acquisition_temp - 1) % 60;
        temps_acquisition = temps_acquisition_temp / 2;
      }
    }
    
  }

  else if ((action_encoder == 1) and (val_choisie == 0) and (Menu_State == 3)) {

    if (State != Old_State)
    {
      if (digitalRead(encoder0PinB) != State)
      {
        val_R2_temp = (val_R2_temp + 1) % 100;
        val_R2 = val_R2_temp / 2;
      }
      else {
        val_R2_temp = (val_R2_temp - 1) % 100;
        val_R2 = val_R2_temp / 2;
      }
    }
  }
}


// doEncoderButton is activated when the button is clicked and affects a variable Menu_State with the encoder0Menu value, also checks if the time is chosen when the third menu is activated
void doEncoderButton() {

  if (action_encoder == 0) {
    Menu_State = encoder0Menu ;
    action_encoder = 1 ;
    }

  else if ((action_encoder == 1) and (Menu_State == 2)) {

    if (temps_choisi == 0) {
      temps_choisi = 1;
    }

    else if (temps_choisi == 1) {
      action_encoder = 0 ;
      temps_choisi = 0;
    }
  }

  else if ((action_encoder == 1) and (Menu_State == 3)) {

    if (val_choisie == 0) {
      val_choisie = 1;
    }

    else if (val_choisie == 1) {
      action_encoder = 0 ;
      val_choisie = 0;
      R2 = val_R2;
    }
  }

  else if (action_encoder == 1) {
    action_encoder = 0 ;
  }

  delay(200);
}

  // Fonctions de simplification

void setup_display() {

  display.clearDisplay();
  display.setTextSize(1);      // Normal 1:1 pixel scale
  display.setTextColor(SSD1306_WHITE); // Draw white text
  display.setCursor(0, 0);     // Start at top-left corner
  
}


void setup() {

  Serial.begin(9600);

  // encodeur rotatoire

  pinMode(encoder0PinA, INPUT); 
  digitalWrite(encoder0PinA, HIGH);       // turn on pullup resistor

  pinMode(encoder0PinB, INPUT); 
  digitalWrite(encoder0PinB, HIGH);       // turn on pullup resistor

  pinMode(Switch, INPUT_PULLUP);

  attachInterrupt(digitalPinToInterrupt(3), doEncoder, RISING); 
  attachInterrupt(digitalPinToInterrupt(2), doEncoderButton, FALLING); 


  // Bluetooth

  pinMode(rxPin,INPUT);
  pinMode(txPin,OUTPUT);
  Serial_Phone.begin(baudrate);

  // Oled

  if(!display.begin(SSD1306_SWITCHCAPVCC, SCREEN_ADDRESS)) {
    Serial.println(F("SSD1306 allocation failed"));
    for(;;); // Don't proceed, loop forever
  }
  
  // Show initial display buffer contents on the screen --
  // the library initializes this with an Adafruit splash screen.
  display.display();
  delay(2000); // Pause for 2 seconds

  // Clear the buffer
  display.clearDisplay();
  
} 



void loop() {

  // Encodeur et OLED -> affichage

  if (action_encoder == 0) {
  
    if (encoder0Menu == 0) {
      // affiche les actions possibles du menu choisi
      setup_display();
      display.println(F("MENU 1 : \nReleve de resistance"));
      display.display();
    }
  
    else if (encoder0Menu == 1) {
      setup_display();
      display.println(F("MENU 2 : \nReleve de tension"));
      display.display();
    }
  
    else if (encoder0Menu == 2) {
      setup_display();
      display.println(F("MENU 3 : \nDefinir le temps \nd'aquisition"));
      display.display();
    }
  
    else if (encoder0Menu == 3) {
      setup_display();
      display.println(F("MENU 4 : \nChanger la valeur\nde R2"));
      display.display();
    }  

  }

  // Encodeur et OLED -> action
  
  else if (action_encoder == 1) {
 
    if (Menu_State == 0) {
    
        // Relevé ADC
      voltage_ADC = analogRead(ADCpin) / 4;
        // Bluetooth
      Serial_Phone.write(voltage_ADC);
      delay(500);
      Serial.print(voltage_ADC + String(" "));
      Serial.println(millis());

      resistance = (R1 * (1 + (R3/R2)) * (5 / (voltage_ADC*0.01952)) - R1 - R5) / 1000;

      setup_display();
      display.println("Resistance : ");
      if (resistance != 0) {
        display.print(resistance);
        display.println(" MOhm  - Envoi BT");
      }
      else {
        display.print("Infini");
        display.println("   - Envoi BT");
      }
      display.println("\n        Press to quit");
      display.display();
      
    
    }
  
    else if (Menu_State == 1) {

        // Relevé ADC
      voltage_ADC = analogRead(ADCpin) / 4;
        // Bluetooth
      Serial_Phone.write(voltage_ADC);

      tension = voltage_ADC * 0.01952;
      
      setup_display();
      display.println("Tension : ");
      display.print(tension);
      display.println(" V   - Envoi BT");
      display.println("\n        Press to quit");
      display.display();
      
    }

    else if (Menu_State == 2) {

      if (temps_choisi == 0) {

        setup_display();
        display.println("Temps d'acquisition :");
        display.print(temps_acquisition);
        display.println(" s");
        display.println("\n       Press to chose");
        display.display();

      }

      else if (temps_choisi == 1) {

        setup_display();
        display.println("Temps d'acquisition :");
        display.print(temps_acquisition);
        display.println(" s   - Envoi BT");
        display.println("\n        Press to quit");
        display.display();

        Serial_Phone.write(temps_acquisition);

      }
    
    }
    else if (Menu_State == 3) {

      if (val_choisie == 0) {
    
        setup_display();
        display.println("Valeur de R2 :");
        display.print(val_R2);
        display.println(" kOhm");
        display.println("\n        Press to chose");
        display.display();

      }

      else if (val_choisie == 1) {

        setup_display();
        display.println("Valeur de R2 :");
        display.print(val_R2);
        display.println(" kOhm   - Envoi BT");
        display.println("\n        Press to quit");
        display.display();

        Serial_Phone.write(val_R2);

      }
    }

  }

}

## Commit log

2021-03-10 Programme arduino
2021-03-10 KiCad ajout
    [Shield.kicad_pcb, Shield.sch]
2021-03-12 Tests Arduino
2021-03-15 Programme Arduino OK
2021-03-16 banc de test 3D
    [Piece_Servomoteur.FCStd]
2021-03-16 simplification arduino
2021-03-17 pin rx tx changés Arduino
2021-03-18 piece servo moteur 3D et autres
    [Piece_Servomoteur.FCStd, Pièce servomoteur v2.stl, pièce servomoteur.stl, socle banc de test.FCStd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]
2021-03-19 ajustement arduino
2021-04-14 arduino changes
2021-04-22 Explications application
    [socle final.stl]
2021-04-26 A faire
    [Piece_Servomoteur.FCStd, Pièce servomoteur v2.stl, Shield.kicad_pcb, Shield.sch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]
2021-04-27 modification Arduino et readme
    [Graphiques.xlsx]
2021-04-27 Suppression de répertoires
2021-04-28 Résultats
    [Graphiques.xlsx]
2021-04-29 image servo moteur
2021-05-02 Readme et autres
    [Graphiques.xlsx]
2021-05-02 datasheet et readme
    [Graphiques.xlsx]
2021-05-05 erreurs datasheet
    [Graphiques.xlsx]
